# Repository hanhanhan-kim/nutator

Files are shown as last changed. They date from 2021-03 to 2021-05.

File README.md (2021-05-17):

# Open-Source Nutator

This repository is a ‘fork’ of a project by Dhwani K. Trivedi and Joshua M. Pearce from Michigan Technological University. The original project is not on GitHub, but is instead hosted [here](https://osf.io/bqysc/), on the Open Science Framework. A published paper that describes the original project can found [here](https://www.academia.edu/34589801/Open_Source_3_D_Printed_Nutating_Mixer) or [here](docs/trivedi_pearce_2017.pdf). I am ‘forking’ their project into this repository because I prefer GitHub for version control and open sourcing. 

<!-- ![demo](docs/demo.gif) -->


In this repository, I detail some of the various modifications I made to build this project. For all 3D-printed parts, I used a [Prusa MK3s](https://shop.prusa3d.com/en/3d-printers/180-original-prusa-i3-mk3s-kit.html?gclid=Cj0KCQjwutaCBhDfARIsAJHWnHvx8k-mshW_x2fmi0MGLbitysPgBX_iFMeMSdHa64Brgxne7ESQhUUaAvccEALw_wcB). `.3mf` files for all parts can be found [here](hardware/3MF_prusa_slicer_files/). 

1. Two components are printed with a flexible filament, such as TPU: the dimpled mat and the slit. The original project recommends NinjaFlex, which is an extremely soft type of TPU. NinjaFlex, however, is an absolute pain to print; the softer the material, the more difficult it is to print. I **do *not* recommend printing with NinjaFlex yourself**.  Rather, I suggest the following alternatives:

   1. I recommend getting the slit made at a 3rd party vendor. I found that [Protolabs ](https://www.protolabs.com/services/3d-printing/polyjet/design-guidelines/) was one of the few manufacturers that could make the part out of PolyJet, with a Shore hardness of 30A.  The pricing is also affordable.

   2. I recommend printing a *negative* of the dimpled mat using PLA, and then filling that negative with [2-part silicone](https://www.amazon.com/gp/product/B07V5FFPWC/ref=ppx_yo_dt_b_asin_title_o00_s01?ie=UTF8&psc=1) (credit to [Julian Wagner](https://github.com/julianmwagner) for the idea!). I found this method to be very easy and affordable, and the silicone-making process is completely safe. Just remember to thoroughly mix the silicone parts together. A photo of the finished product is attached below:

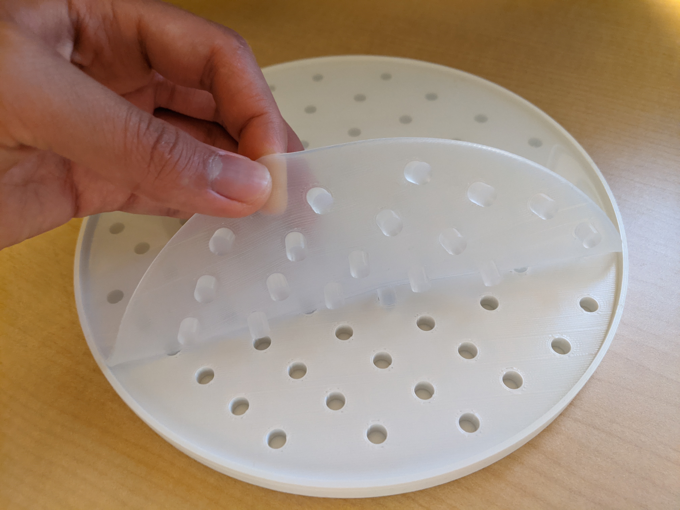
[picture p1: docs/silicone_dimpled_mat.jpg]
silicone_mold
      

2. The reason the slit component must be printed with the softest possible TPU is because the rod piece “leans” into it, while the rod rotates via the motor and skateboard bearing. The extent to which the rod leans into the slit is greatest when the rod points in the same direction as the slit’s long axis. By this logic, the **rod should be printed with the highest possible strength**, so that it doesn’t snap during the nutator’s operation. Adjust the slicer settings for the rod such that both the infill and the perimeter values are high. The attached [`rod.3mf`](hardware/3MF_prusa_slicer_files/rod.3mf) file provides settings for Prusament PLA; the material can be easily adjusted. If you want to be really excessive, you can send the rod component to a 3rd party service like [Shapeways](https://www.shapeways.com/), and have it printed in something like [steel](https://www.shapeways.com/materials/steel/), for 40 USD or so (see the final note on pricing)

3. I adjusted the orientations of some of the 3D-printed components, and added supports when appropriate. The `.3mf` files contain all the slicer information, and are superior to `.stl` file types. See [this informative video](https://www.youtube.com/watch?v=BABdR9d8Cp4&ab_channel=Prusa3DbyJosefPrusa) for more details on `.3mf` vs `.stl`. 

4. I replaced some of the original materials from the BOM because I had difficulty finding some of the listed components—most of which were from Amazon. The commercial parts I used are:

   | Part                 | Source                                                       | Price (USD)                     | Notes                                                        |
   | -------------------- | ------------------------------------------------------------ | ------------------------------- | ------------------------------------------------------------ |
   | DPDT switch          | DigiKey [CKN11630-ND](https://www.digikey.com/en/products/detail/c-k/7201J26ZBE22/3729342?s=N4IgTCBcDaIMYGsB2BGFA2AzABgLRIBMQBdAXyA) | 14.07                           | I couldn’t find the DPDT switch linked in the original article. This switch from DigiKey is pricey, but it’s been tested for 100 000 cycles at full load, and more importantly, I like the tactile feel of paddle switches. Pretty much any switch with 20.32mm x 12.70mm panel cutuout dimensions should work. [Here](https://www.digikey.com/en/products/filter/rocker-switches/195?s=N4IgjCBcoOwBwGYqgMZQGYEMA2BnApgDQgD2UA2iAgJwAsYADDCALrEAOALlCAMqcAnAJYA7AOYgAvtKA) are the DigiKey search results, given the dimensions. Any of those switches should work. |
   | DC female power jack | Amazon<br />ASIN [B01N8VV78D](https://www.amazon.com/gp/product/B01N8VV78D/ref=ppx_od_dt_b_asin_title_s00?ie=UTF8&psc=1) | 7.99 / 12                       | I found the dimensions of these 2.1 mm panel-mounted female DC power jack sockets to work perfectly. I might need to replace these parts in the future with something that can be more reliably sourced. |
   | Skateboard bearing   | Amazon<br />ASIN [B08DDJBJVH](https://www.amazon.com/gp/product/B077FN9ZNT/ref=ppx_yo_dt_b_search_asin_title?ie=UTF8&psc=1) | 24.99 / 10                      | Any 608 skateboard bearings should work.                     |
   | DC motor             | Amazon<br />ASIN [B01N1JQFYX](https://www.amazon.com/gp/product/B01N1JQFYX/ref=ppx_yo_dt_b_asin_title_o08_s00?ie=UTF8&psc=1) | 15.49                           | This 12 V worm gear motor is the exact model that the original project recommends. This motor can still be sourced from Amazon USA as of 2021-03-20. |
   | M3 screws            | McMaster-Carr<br />[91290A111](https://www.mcmaster.com/91290A111/)<br />and <br />McMaster-Carr<br />[ 91290A115](https://www.mcmaster.com/91290A115/) | 8.71 / 100 x 4 + 7.71 / 100 x 3 | For the M3 screws, I used 6 mm long screws for everything except when securing the bearing holder to the motor shaft, and the the cover to the base. For those parts, I used 10 mm long screws. |
   | M3 nuts              | McMaster-Carr <br />[90592A085](https://www.mcmaster.com/90592A085/) | 0.88 / 100 x 5                  | Regular M3 nuts.                                             |

   Estimated total cost, not including 3D printer filament, is: **$33.35 USD**. 

5. Out of laziness, I opted not to redesign any of the 3D-printed parts. All the parts seem fine for the most part, but the one thing that annoys me is that for the 3D-printed base, the parts that hold the nuts to secure the cover are quite large. I would shrink the perimeters of the nut-securing insets, such that they’re more or less exactly the dimensions of the nut, and then I’d pull the nut in with a screw from the opposite side, to establish a captive nut. See step 9 of [this article](https://help.prusa3d.com/en/guide/1-introduction_54032) for an explanation. In the meantime, a careful dab of hot glue works fine. 

6. I generated an [alternative mat](hardware/3MF_prusa_slicer_files/flex_dimpled_mat_beetles_flies.3mf) for the nutator that features a contentious message for some researchers in the biological sciences. 

7. Some additional upgrades that can be made to the nutator include:

   - Adding a cheap ready-made PWM circuit. Tons of varieties are available on Amazon. 
   - Attaching some kind of microcontroller, such as one that can connect to the internet (some kind of ESP module), so that timers can be set from a phone app. 
   - Attaching some kind of sensor that checks that the motor is rotating. We can use something as simple as a reed switch that triggers every set period. If the reed switch fails to change state before the set period, then some kind of message can be sent to some phone app, to inform the user. 
   - Preparing parts so that the nutator can be used in a 4 C fridge. I might seal exposed electronics with something like heat shrink wrap and UV-curable glue, and opt for corrosion-resistant screws, like the [92290A1XX](https://www.mcmaster.com/screws/socket-head-screws/socket-head-screws-6/super-corrosion-resistant-316-stainless-steel-socket-head-screws/system-of-measurement~metric/thread-size~m3/) series screws from McMaster (where XX is 09 to 31). Some parts, like the internals of the DC motor, might preclude straightforward protection from extreme humidity. Room temperature operation is probably ideal. 

Some of the above changes I made or suggested increase the price of the nutator. Commercial scientific nutators, however, begin at something like [500 USD](https://www.thomassci.com/Equipment/Ambient-Temperature-Shakers/_/Nutating-3D-Platform-Mixer-Nutating-3D-shaker-with-dimpled-rubber-mat?q=Nutator), so making a few ‘premium’ upgrades doesn’t really merit a cost-benefit analysis. 

As of 2021-03-21, I’ve continuously rotated the nutator for __ hours, and then stopped, out of boredom.

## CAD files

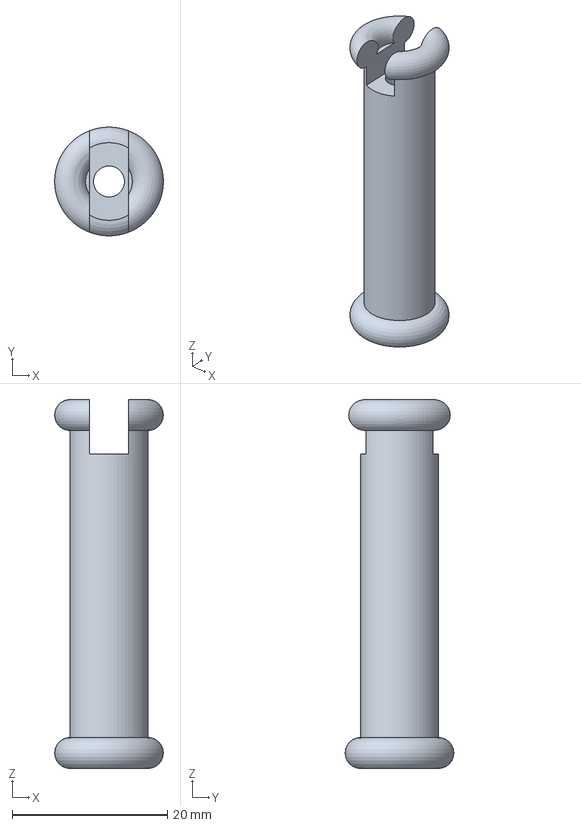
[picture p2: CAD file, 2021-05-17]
hardware/3MF_prusa_slicer_files/ninjaflex_slit.3mf
14.0 x 14.0 x 47.5 mm

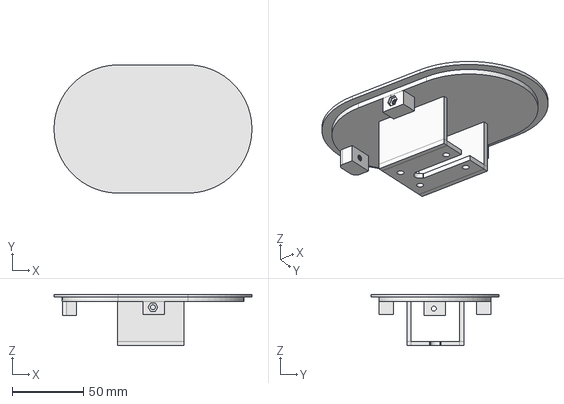
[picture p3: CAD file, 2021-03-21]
hardware/FreeCAD_files/base.FCStd
139.2 x 90.1 x 36.0 mm

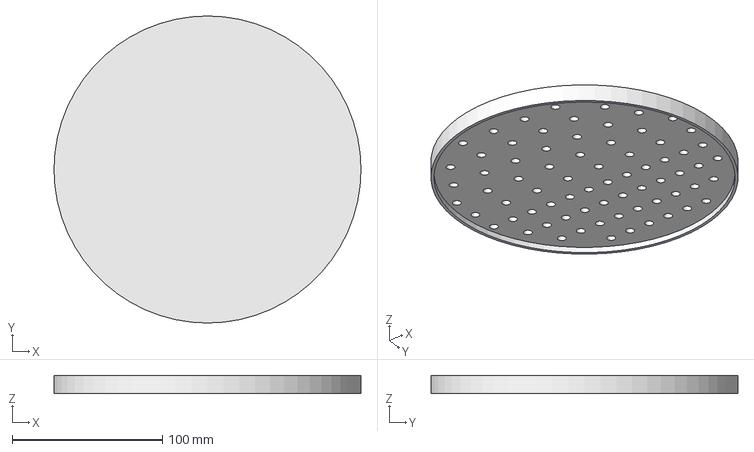
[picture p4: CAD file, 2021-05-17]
hardware/STEP_files/dimpled_mat_negative.step
204.0 x 204.0 x 12.0 mm

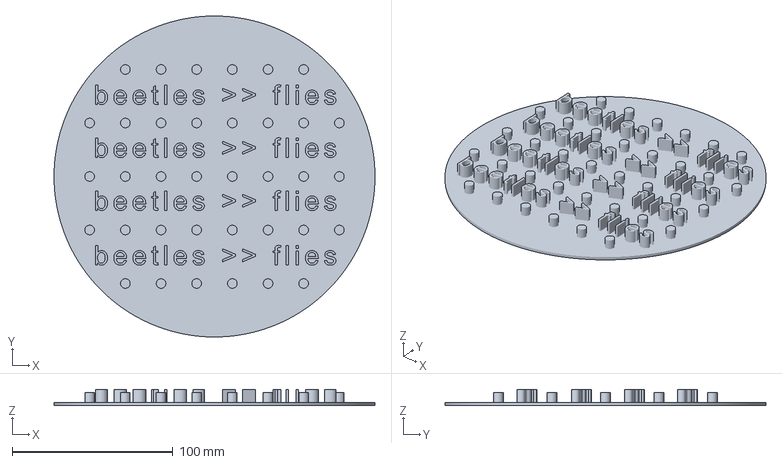
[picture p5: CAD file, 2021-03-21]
hardware/3MF_prusa_slicer_files/fillamentum_flex_98a_dimpled_mat_beetles_flies.3mf
200.0 x 200.0 x 10.0 mm

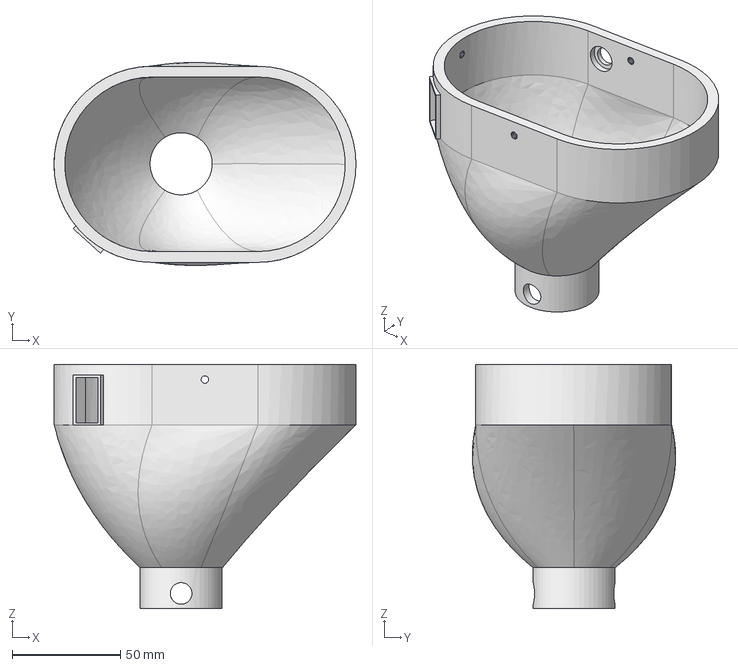
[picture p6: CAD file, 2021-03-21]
hardware/FreeCAD_files/cover.FCStd
139.8 x 94.1 x 113.0 mm

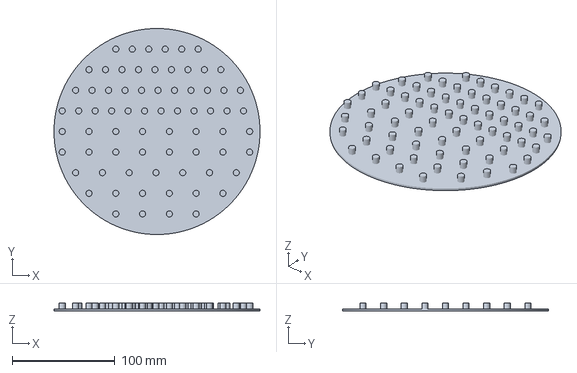
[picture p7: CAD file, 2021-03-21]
hardware/3MF_prusa_slicer_files/fillamentum_flex_98a_dimpled_mat.3mf
200.0 x 200.0 x 8.00 mm

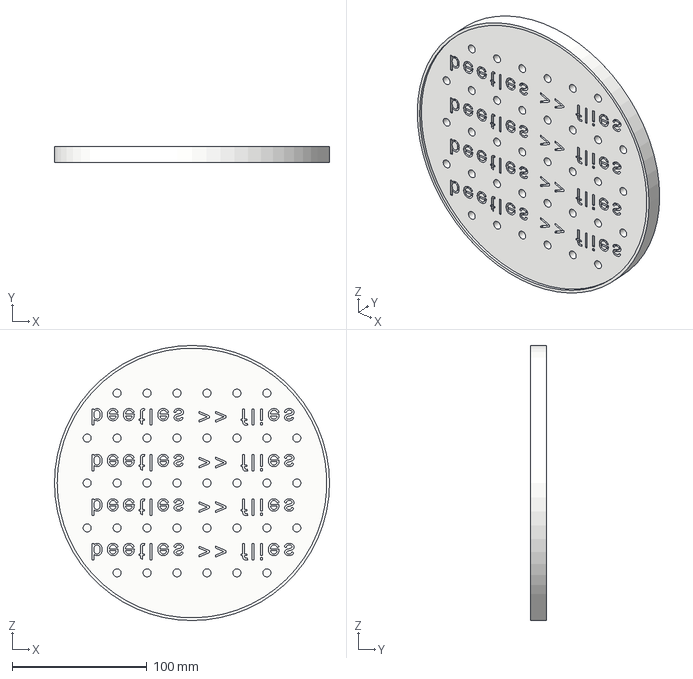
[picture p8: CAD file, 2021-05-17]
hardware/STEP_files/dimpled_mat_beetles_flies_negative.step
204.0 x 12.0 x 204.0 mm

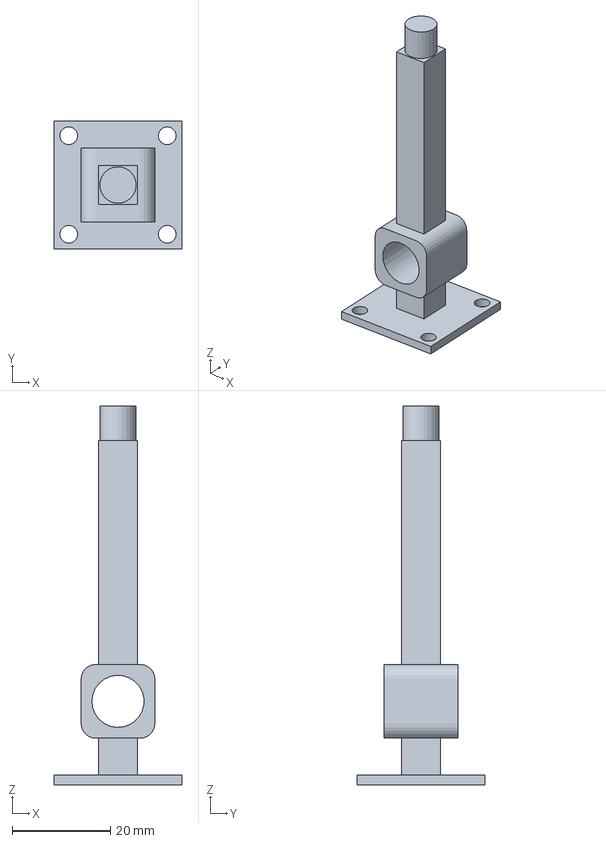
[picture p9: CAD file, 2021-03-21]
hardware/3MF_prusa_slicer_files/rod.3mf
26.0 x 26.0 x 77.0 mm

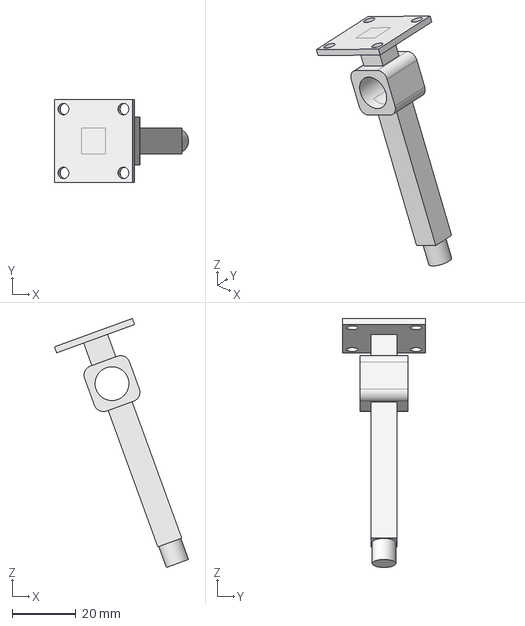
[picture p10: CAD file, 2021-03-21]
hardware/FreeCAD_files/rod.FCStd
42.0 x 26.0 x 78.1 mm

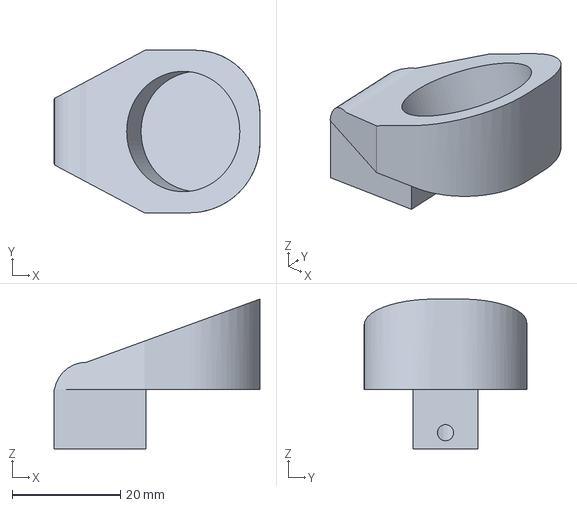
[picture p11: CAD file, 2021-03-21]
hardware/3MF_prusa_slicer_files/bearing_holder.3mf
38.0 x 30.0 x 27.6 mm

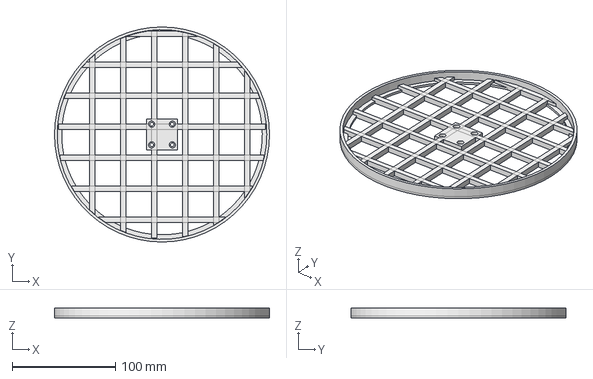
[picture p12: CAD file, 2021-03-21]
hardware/FreeCAD_files/platform.FCStd
208.0 x 208.0 x 10.0 mm

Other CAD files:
hardware/STEP_files/ninajflex_slit.step
hardware/FreeCAD_files/ninjaflex_slit.FCStd
hardware/3MF_prusa_slicer_files/base.3mf
hardware/FreeCAD_files/flex_dimpled_mat.FCStd
hardware/FreeCAD_files/bearing Holder.FCStd
hardware/3MF_prusa_slicer_files/cover.3mf
hardware/3MF_prusa_slicer_files/platform.3mf
hardware/STL_files/base.stl
hardware/STL_files/bearing_holder.stl
hardware/STL_files/cover.stl
hardware/STL_files/dimpled_mat_beetles_flies_negative.stl
hardware/STL_files/dimpled_mat_negative.stl
hardware/STL_files/ninjaflex_slit.stl
hardware/STL_files/platform.stl
hardware/STL_files/rod.stl

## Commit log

2021-03-21 update readme and add hardware files
    [base.3mf, base.FCStd, base.stl, bearing Holder.FCStd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]
2021-03-21 add beetles >> flies mat, and fix typos in readme
    [flex_dimpled_mat_beetles_flies.3mf, flex_dimpled_mat_beetles_flies.step, flex_dimpled_mat_beetles_flies.stl]
2021-04-25 update slit material and add demo gif
2021-05-17 update with new process for flex parts
    [dimpled_mat_beetles_flies_negative.step, dimpled_mat_beetles_flies_negative.stl, dimpled_mat_negative.step, dimpled_mat_negative.stl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]
